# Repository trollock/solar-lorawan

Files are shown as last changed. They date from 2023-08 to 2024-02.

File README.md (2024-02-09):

# Repository Introduction

The following repository contains all of the necessary hardware, software, TTN interface, 3D printing files, and assembly instructions for the CMWX-based LoRaWAN GPS radiotransmitter.

# 1. Hardware 

- datasheets for individual components found in subfolder https://github.com/trollock/solar-lorawan/tree/main/3_hardware

- design files found in subfolder https://github.com/trollock/solar-lorawan/tree/main/5_design_files
- produced in Autodesk Fusion 360 in *.fsch, *.fbrd, and *.f3z formats
  
- production settings:
  + 24.9 x 10.5 mm, 2 layers, 0.4 mm FR4, 0.2 mm min hole size, immersion gold (ENIG) surface finish (1U"), 0.06 mm min track spacing, 1 oz Cu finished copper



# 2. LoRaWAN Network IDs 

- Example based on connecting to The Things Network (TTN) for Europe EU868 Band
- Create a free TTN User account (not the Things Stack)
  + Become familiar with the basics of LoRa and LoRaWAN https://www.thethingsnetwork.org/docs/lorawan/

- Create an application for your devices

- Registering a new device
  + Click "_Enter the device specifics manually_" radio button
  + Click the frequency plan "_Europe 863-870 MHz (SF9 for RX2 - recommended)_"
  + Click the LoRaWAN version "_LoRaWAN Specification 1.0.2_"
  + Click the Regional Parameters version "_RP001 Regional Parameters 1.0.2 revision B_"
  + Create a unique 64 bit JoinEUI for your device (can be shared amongst devices, can be random)  
  + Click "_Generate_" to create a 64-bit random DevEUI
  + Click "_Generate_" to create a 128-bit random AppKEY (can be shared amongst devices)
    + Keep the JoinEUI, DevEUI, and AppKEY to copy into the Arduino example file  
  + Click "_Register End Device_" to create your new device
  
  + see example image below 



# 3. Programming 

- programmed using a combination of Arduino, STM32CubeProgrammer, and an ST-Link.
  + *.elf files are first generated in Arduino, then loaded into STM32CubeProgrammer connected via an ST-Link 
- built on the Arduino core found here https://github.com/GrumpyOldPizza/ArduinoCore-stm32l0
  + comfirmed using a Mac running macOS Big Sur
- basic arduino example found in subfolder XXXX
  + can be modified and them compiled

## Basic programming example

- Open the default example in Arduino IDE found in subfolder "sample_software" https://github.com/trollock/solar-lorawan/tree/main/4_software
- Copy and paste the correct JoinEUI, DevEUI, and AppKEY created earlier under "_Registering a new device_"
  + This can be found on lines 42 - 46 of the example *.ino file provided.
 
  + see example image below



  + click "verify" and then find path to location of *.elf file
  + before opening STM32CubePorgrammer, connect the ST-Link to a suitable port
    + confirm the ST-Link is connected in STM32CubeProgrammer in the upper right under "ST-Link configuration"
  + provide 3.3v power to the device and click "Connect" in STM32CubeProgrammer
  + click "Open File" in STM32CubeProgrammer and find the location of the *.elf file generated earlier by Arduino
  + click "Download" in STM32CubeProgrammer and wait ~ 2-3 seconds until finished 
  + click "Disconnect" in STM32CubeProgrammer
 
  + see example image below
 
  compile

# 4. 3D Printed Housing

- design files for 3D printed housings found in subfolder https://github.com/trollock/solar-lorawan/tree/main/6_housings
- printed on Formlabs Form 3+ / 3B+ at a 0.05 mm micron layer height
- *.stl file sliced in Preform 3.33.1
  + sample print file with supports provided

- Version A for IXOLAR KXOB based solar cells (with PCB adapter)

Housing_A

- Version B for raw GaInAs triple junction solar cells (no adapter necessary)

# 5. Assembly

# 6. Data Access

- log into your new TTN account and click on your application

- Payload Formatter
  + copy the data from the file "payload_formatter_uplink.txt" in the subfolder 2_scripts https://github.com/trollock/solar-lorawan/tree/main/2_scripts
  + click "formatter type" and select Custom Javascript formatter.
  + Delete the code in the paylod formatter box
  + Paste the data from the file "payload_formatter_uplink.txt"
  + Click "Save Changes"

  + see example image below
    


- Storage Integration
  + Click on the leftside menu "Integrations" and then click "Storage Integration"
  + Cliack on the radio button "Activate Storage Integration"
  + The status should say "The storage integration is currently activated"

- API Keys
  + API keys are used for accessing the storage API in a secure manner from another process or service (e.g. [R] )
  + Click the radio button "+ Add API Key"
  + Save this information in a secure place for later
 
- 
- files for accessing stored

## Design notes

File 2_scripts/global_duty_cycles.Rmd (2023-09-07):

---
title: "TTFF / Warm Fixes"
author: "XXXXXX"
date: '2023-05-03'
output: html_document
---

```{r setup, include=FALSE}
knitr::opts_chunk$set(echo = TRUE)

require(readr)
require(tidyverse)
require(ggplot2)
```

```{r, include=FALSE}
df <- list.files(path="//Users/ryanshipley/Documents/Research/2023_CMWX_Radiotags/Data", full.names = TRUE) %>% 
  lapply(read_csv) %>% 
  bind_rows %>%
  dplyr::mutate(time_stamp = lubridate::ymd_hms(message_time)) %>%
  dplyr::distinct(time_stamp, .keep_all=TRUE) %>%
  dplyr::filter(latitude > 0)
```

```{r}
df <- df %>%
  group_by(id) %>%
  arrange(message_time, .by_group = TRUE) %>%
  mutate(time_to_fix = message_time - lag(message_time, default = first(message_time)))
         
df$time_to_fix <- as.numeric(df$time_to_fix)

df$interval <- 
  ifelse (df$time_to_fix > 600 & df$time_to_fix < 800, 
      10,
  ifelse(df$time_to_fix > 1200 & df$time_to_fix < 1400, 
      20,
  ifelse (df$time_to_fix > 1800 & df$time_to_fix < 2000,
      30,
  ifelse (df$time_to_fix > 3600 & df$time_to_fix < 3900,
      60,
  ifelse (df$time_to_fix > 7200 & df$time_to_fix < 7400,
      120,
  ifelse (df$time_to_fix > 10800 & df$time_to_fix < 11200,
      180,
  ifelse (df$time_to_fix > 21600 & df$time_to_fix < 21800,
      360,
      NA)))))))

df$time_to_fix <- 
  ifelse (df$time_to_fix > 600 & df$time_to_fix < 800, 
      df$time_to_fix - 600,
  ifelse(df$time_to_fix > 1200 & df$time_to_fix < 1400, 
      df$time_to_fix - 1200,
  ifelse (df$time_to_fix > 1800 & df$time_to_fix < 2000,
      df$time_to_fix - 1800,
  ifelse (df$time_to_fix > 3600 & df$time_to_fix < 3900,
      df$time_to_fix - 3600,
  ifelse (df$time_to_fix > 7200 & df$time_to_fix < 7400,
      df$time_to_fix - 7200,
  ifelse (df$time_to_fix > 10800 & df$time_to_fix < 11200,
      df$time_to_fix - 10800,
  ifelse (df$time_to_fix > 21600 & df$time_to_fix < 21800,
      df$time_to_fix - 21600,
      NA)))))))

df <- df %>%
      filter(time_to_fix < 180)
```

```{r}
ggplot(df, aes(as.factor(hdop),time_to_fix))+
  geom_boxplot()
```

```{r}
fix_summary <- df %>%
            group_by(interval) %>%
            summarize(n = n(), mean = mean(time_to_fix, na.rm=T), sd = sd(time_to_fix, na.rm=T))
```

```{r}
require(sf)

start <- data.frame(lat = c(46.83353642366947),
                    lon = c(8.182752723850907)) %>% 
  sf::st_as_sf(coords = c("lon", "lat"), crs = 4326)

df <- df %>%
        sf::st_as_sf(coords = c("longitude", "latitude"), crs = 4326)

distance <- data.frame(distance = t(sf::st_distance(start, df, by_element = FALSE)))

df <- cbind(df, distance)

acc_summary <- df %>%
            group_by(hdop) %>%
            summarize(n = n(), mean = mean(distance, na.rm=T), sd = sd(distance, na.rm=T)) 

centroid_summary <- df %>%
            group_by(hdop) %>%
            summarize(geometry = st_union(geometry)) %>% 
            st_centroid

cents <- as.data.frame(st_coordinates(centroid_summary))

centroid_summary <- cbind(centroid_summary, cents)

centroid_distance <- data.frame(distance = t(sf::st_distance(start, centroid_summary, by_element = FALSE)))

```

```{r}
start2 <- st_transform(start, crs = 28992)
start2 <- as.data.frame(st_coordinates(start2))

df2 <- st_transform(df, crs = 28992)
df2 <- as.data.frame(st_coordinates(df2))

df2$X <- df2$X - start2$X
df2$Y <- df2$Y - start2$Y
 
df <- cbind(df, df2)
```

```{r}
require(ggdensity)
require(ggforce)
library(magrittr)

# constants
axis_begin  <- -350
axis_end    <- 350
total_ticks <- 11

# chart junk data
tick_frame <- 
  data.frame(ticks = seq(axis_begin, axis_end, length.out = total_ticks), 
             zero=0) %>%
  subset(ticks != 0)

lab_frame <- data.frame(lab = seq(axis_begin, axis_end, length.out = total_ticks),
                        zero = 0) %>%
  subset(lab != 0)

tick_sz <- (tail(lab_frame$lab, 1) -  lab_frame$lab[1]) / 128

```

```{r}
ggplot(df, aes(X,Y)) + 
    # CHART JUNK
  # y axis line
  geom_segment(x = 0, xend = 0, 
               y = lab_frame$lab[1], yend = tail(lab_frame$lab, 1),
               size = 0.25, color="grey90") +
  # x axis line
  geom_segment(y = 0, yend = 0, 
               x = lab_frame$lab[1], xend = tail(lab_frame$lab, 1),
               size = 0.25, color="grey90") +
  # x ticks
  geom_segment(data = tick_frame, 
               aes(x = ticks, xend = ticks, 
                   y = zero, yend = zero + tick_sz), color="grey90") +
  # y ticks
  geom_segment(data = tick_frame, 
               aes(x = zero, xend = zero + tick_sz, 
                   y = ticks, yend = ticks), color="grey90") + 
  geom_circle(aes(x0 = 0, y0 = 0, r = 140), inherit.aes = FALSE, color="grey90", linetype="dotted") +
  geom_circle(aes(x0 = 0, y0 = 0, r = 210), inherit.aes = FALSE,  color="grey90", linetype="dotted") +
  geom_circle(aes(x0 = 0, y0 = 0, r = 280), inherit.aes = FALSE,  color="grey90", linetype="dotted") +
  geom_point(size=0.01, color="grey50") +
  geom_hdr_lines(data=df[ which(df$hdop == 30), ],  method="freqpoly",  aes(X,Y), color="#440154", size=0.5, probs=0.90, n=500, alpha=0.75) +
  geom_hdr_lines(data=df[ which(df$hdop == 20), ],  method="freqpoly",  aes(X,Y), color="#29af7f", size=0.5, probs=0.90, n=500, alpha=0.75) +
  geom_hdr_lines(data=df[ which(df$hdop == 10), ], method="freqpoly",  aes(X,Y), color="#FDE725", size=0.5, probs=0.90, n=500, alpha=0.75) +
  theme_void()+
  coord_fixed(xlim=c(-350, 350), ylim=c(-350, 350)) +
    # labels
  geom_text(data=lab_frame, aes(x=lab, y=zero, label=lab),
            family = 'Arial', vjust=1.5, color="grey70") +
  geom_text(data=lab_frame, aes(x=zero, y=lab, label=lab),
            family = 'Arial', hjust=1.25, color="grey70")
```

```{r}
setwd("//Users/ryanshipley/Documents/Research/2023_CMWX_Radiotags/Lab_Light_Measurements")

irr <- read.csv("irradiance.csv")

irr_mdl <- glm(Power ~ Irradiance, data=irr)

energy_plot <- ggplot(data=irr, aes(Power / 1000, Irradiance)) +
  geom_smooth(se=FALSE, color="grey80", size=0.5) +
  geom_jitter(size=0.2)+
  cowplot::theme_cowplot() +
  ylab(expression(Irradiance ~ W/m^-2)) +
  xlab ("Charge Current (mA)") +
  scale_x_log10()+
  scale_y_log10()+
  annotation_logticks()+
  geom_hline(yintercept = 75, linetype="dotted", color="grey80") + 
  geom_hline(yintercept = 175, linetype="dotted", color="grey80") + 
  geom_hline(yintercept = 500, linetype="dotted", color="grey80")

energy_plot

```

```{r}
# install and load the solrad package
#install.packages("solrad")
library(solrad)

DOY <- seq(-1, 365, .01)

# define the latitude range
lat_range <- seq(-90, 90, by = 0.5)

# loop over latitudes to calculate irradiance for each time step
irradiance_data <- lapply(lat_range, function(lat) {
  radiation <- OpenRadiation(DOY, Lat = lat, Lon=0, SLon=0, DS=0, Elevation = 100)
})

# combine the results into a matrix
#irradiance_matrix <- matrix(do.call(cbind, irradiance_data))

#irradiance_matrix <- oce::matrixSmooth(irradiance_matrix, 500)

irradiance_matrix <- as.data.frame(do.call(cbind, irradiance_data))

# set the row names as latitude values
row.names(irradiance_matrix) <- DOY

# set the column names as datetime values
colnames(irradiance_matrix) <- lat_range

irradiance_matrix <- cbind(DOY, irradiance_matrix)

irradiance_matrix <- reshape2::melt(irradiance_matrix, id=c("DOY"))

irradiance_matrix$DOY_bin <- ceiling(irradiance_matrix$DOY)

irradiance_summary <- irradiance_matrix %>%
                        dplyr::group_by(DOY_bin, variable) %>%
                        dplyr::summarize(mean = mean (value, na.rm=T)) %>%
                        dplyr::filter(DOY_bin > 0) %>%
                        dplyr::filter(mean > 0)

irradiance_summary <- irradiance_summary %>%
                        pivot_wider(names_from = variable, values_from = mean)

irradiance_summary <- as.matrix(irradiance_summary[, -1])

irradiance_summary <- oce::matrixSmooth(irradiance_summary, 3)

colnames(irradiance_summary) <- lat_range

irradiance_summary <- as.data.frame(cbind(DOY = seq(1,365, 1), irradiance_summary))

irradiance_summary <- reshape2::melt(irradiance_summary, id=c("DOY"))

irradiance_summary <- irradiance_summary %>%
                        dplyr::filter(!is.na(value))

irradiance_summary$variable <- as.numeric(levels(irradiance_summary$variable))[irradiance_summary$variable]
```

```{r}
cold_fix_mean <- 45

irradiance_summary$harv_30 <- ifelse(irradiance_summary$value == 0, 0, ((irr_mdl$coefficients[2] * (irradiance_summary$value)) - irr_mdl$coefficients[1]) * 0.3)
irradiance_summary$time_fx_30 <- ifelse(irradiance_summary$harv_30 == 0, 0, 1440 / (((cold_fix_mean * 32000) / irradiance_summary$harv_30 ) / 60 ))
 
irradiance_summary$harv_05 <- ifelse(irradiance_summary$value == 0, 0, ((irr_mdl$coefficients[2] * (irradiance_summary$value)) - irr_mdl$coefficients[1]) * 0.05)
irradiance_summary$time_fx_05 <- ifelse(irradiance_summary$harv_05 == 0, 0, 1440 / (((cold_fix_mean * 32000) / irradiance_summary$harv_05 ) / 60 ))

duty_01_plot <- ggplot(irradiance_summary, aes(DOY, variable, z=time_fx_05)) +
                geom_raster(fill="white", color="white") +
                #geom_contour(aes(colour = after_stat(level))) +
                metR::geom_contour2(aes(z = time_fx_05, label = stat(level), colour = after_stat(level)), breaks=c(6,8,10,12,14,16,18,20,22,24,26)) +
  scale_colour_viridis_c() + 
                cowplot::theme_cowplot() +
                xlab("Day of Year") +
                ylab( "Latitude") +
  theme(legend.position = "none") +
  scale_y_continuous(expand = c(0,0), breaks=c(-90, -60, -30, 0 , 30, 60, 90)) +
  scale_x_continuous(expand = c(0,0), breaks=c(1, 60, 120, 180, 240, 300, 360)) +
  theme(panel.background = element_rect(fill = 'grey80', colour = 'grey80'))

duty_01_plot
```

```{r}
cowplot::plot_grid(energy_plot, duty_01_plot, align = 'h')
```

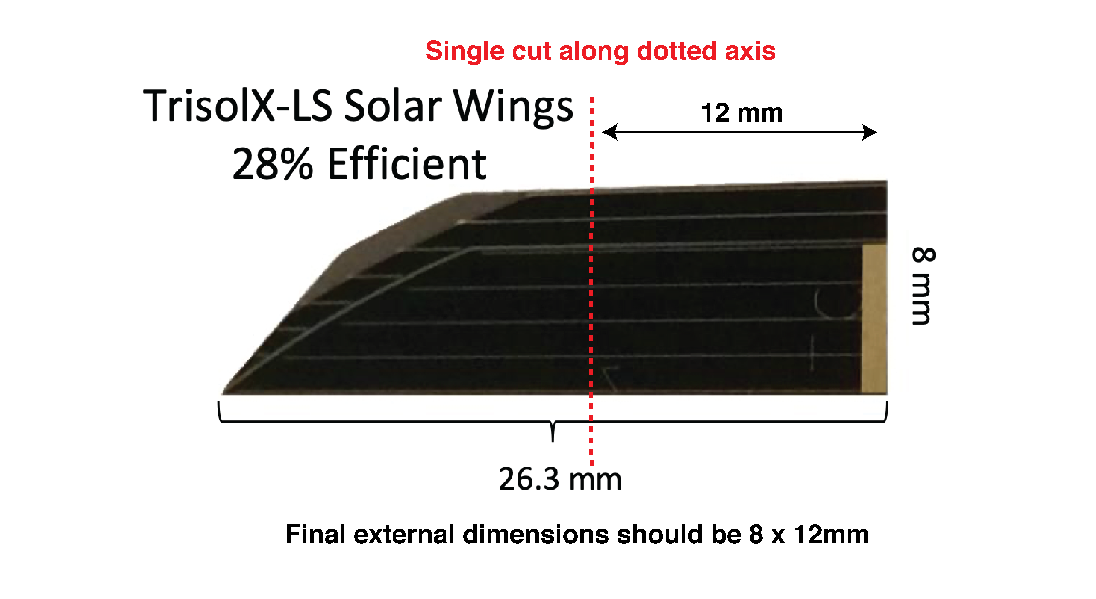
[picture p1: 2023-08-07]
3_hardware/TrisolX/Cut Dimensions/TrisolX.png

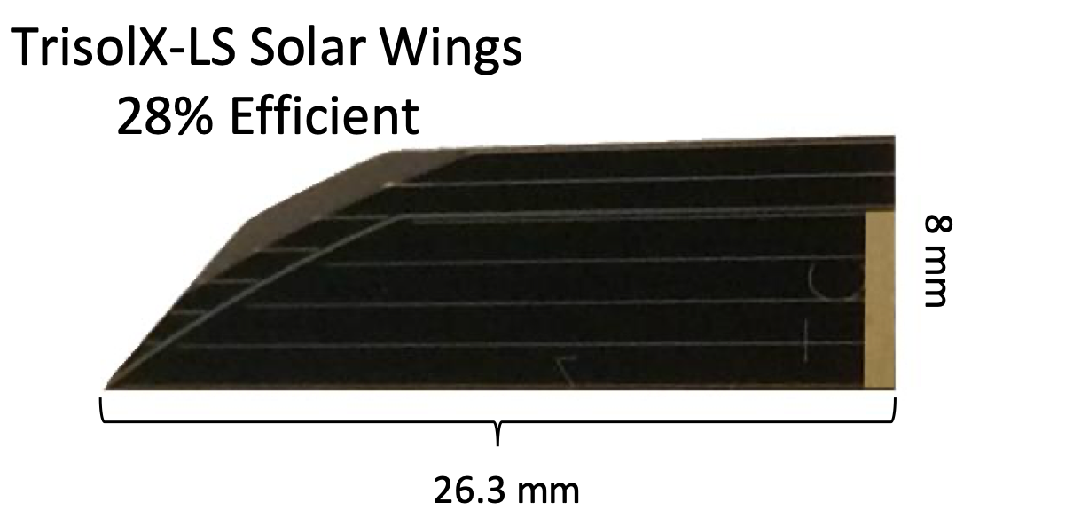
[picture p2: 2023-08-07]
3_hardware/TrisolX/Screen Shot 2023-04-20 at 6.27.21 PM.png

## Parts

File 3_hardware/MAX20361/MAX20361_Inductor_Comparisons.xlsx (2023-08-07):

Inductors for the MAX201361
Recommended
Manufacturer | Part Number | Inductance | V | I | Isat | DCR | Resonance | Dimensions
Murata | DFE201612E-4R7M=P2 | 4.7 | 20 | 1.2 | 1.8 | 0.252 | 1 MHz | 2 x 1.6 x 2
Murata | DFE252010F-4R7M=P2 | 4.7 | 20 | 1.4 | 1.9 | 0.24 | 1 MHz | 2.5 x 2 x 1
Wurth | 744043004 | 4.7 |  | 1.55 | 1.7 | 0.05 | 60 MHz | 4.8 x 4.8 x 3
Wurth | 744031150 | 15 |  | 0.45 | 0.62 | 0.255 | 30 MHz | 3.8 x 3.8 x 1.8
Wurth | 7447779122 | 22 | 120 | 1.41 | 1.7 | 0.09 | 17 MHz | 7.3 x 7.3 x 4.5
Coildcraft | XFL2010-223MR | 22 |  | 0.16 | 0.31 | 1.3 |  | 2.0 x 1.0
Coilcraft | LPS3015-223MR | 22 |  | 0.42 | 0.5 | 0.83 |  | 3.13 x 3.13 x 1.5
Coilcraft | LPS3030-223 | 22 |  | 0.42 | 0.48 | 0.31 |  | 3.15 x 3.15 x 3
Murata | LQH44PN220MPR# (https://www.murata.com/en-global/products/productdetail?partno=LQH44PN220MPR%23) | 22 |  | 0.9 | 1.05 | 0.348 |  | 4 x 4 x 1.65
Wurth | 744031220 | 22 |  | 0.36 | 0.51 | 0.41 |  | 3.8 x 3.8 x 1.8
Wurth | 744025220 | 22 |  | 0.5 | 0.75 | 0.525 |  | 2.8 x 2.8 x 2.8
Wurth | 744043220 | 22 |  | 0.7 | 0.925 | 0.16 |  | 4.8 x 4.8

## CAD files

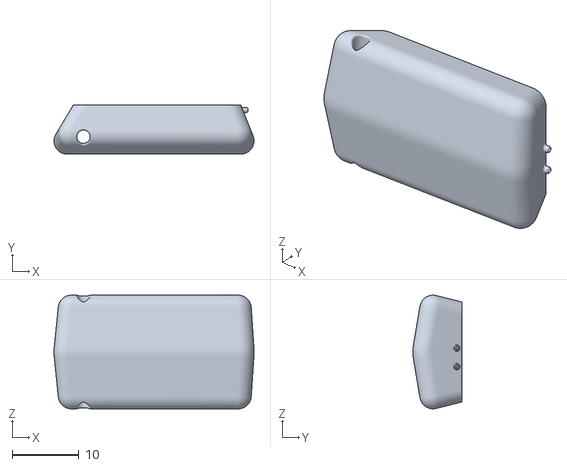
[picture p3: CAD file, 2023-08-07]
6_housings/v27_housing.stl
30.0 x 7.43 x 17.1

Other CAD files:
3_hardware/TrisolX/TrisolX_cell.dwg

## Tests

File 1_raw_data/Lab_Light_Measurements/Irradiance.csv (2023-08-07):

Irradiance | Irr2 | Power | Power2
52 | 52 | 245 | 227
52 | 49 | 240 | 227
52 | 48 | 243 | 256
52 | 51 | 249 | 258
52 | 57 | 237 | 248
68 | 72 | 488 | 456
68 | 65 | 481 | 446
68 | 71 | 493 | 501
68 | 63 | 499 | 510
68 | 71 | 483 | 497
84 | 81 | 740 | 794
84 | 91 | 743 | 772
84 | 81 | 732 | 672
84 | 77 | 728 | 724
84 | 87 | 734 | 744
103 | 109 | 1022 | 1049
103 | 102 | 1026 | 1113
103 | 111 | 1031 | 1084
103 | 108 | 1018 | 975
103 | 112 | 1027 | 970
126 | 121 | 1379 | 1244
126 | 120 | 1374 | 1295
126 | 134 | 1383 | 1447
126 | 123 | 1372 | 1375
126 | 127 | 1382 | 1340
163 | 153 | 1945 | 1896
163 | 152 | 1932 | 2006
163 | 158 | 1936 | 1772
163 | 172 | 1951 | 1787
163 | 149 | 1953 | 2052
219 | 228 | 2805 | 2736
219 | 236 | 2793 | 2569
219 | 214 | 2799 | 2857
219 | 239 | 2808 | 2647
219 | 215 | 2807 | 2534
276 | 274 | 3677 | 3389
276 | 293 | 3663 | 3833
276 | 253 | 3689 | 3459
276 | 253 | 3672 | 3937
276 | 285 | 3667 | 3745
331 | 305 | 4520 | 4145
331 | 310 | 4511 | 4062
331 | 308 | 4518 | 4729
331 | 335 | 4532 | 4388
331 | 305 | 4529 | 4833
435 | 446 | 6101 | 5934
435 | 432 | 6213 | 6270
435 | 456 | 6119 | 6225
435 | 456 | 6202 | 5928
435 | 394 | 6127 | 5800
632 | 639 | 9130 | 8363
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

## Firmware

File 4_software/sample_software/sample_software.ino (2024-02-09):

/* LoRa GPS Receiver (needs a better name)
rev 0.1 J R Shipley 26/12/2020 
The state machine contains 4 basic parts - 1) sleep mode (slp_mode), 2) gps mode (gps_mode), 3) transmit mode (tx_mode) and 
receive mode (rx_mode).
We will use a set of different basic counters to determine how long it should attempt to obtain a gps fix 
In the future, it would be ideal component to implement a simplified version of a PID controller to determine the 
trajectory of the battery charge state, to make basic predictions on future charge states, and the amount of time
that should be dedicated to getting a fix.

Hardware changes 
rev 0.1 - changed the ZOE-M8Q RAM backup to use a dedicated I/O on the CMWX module, so we can turn off 
battery RAM backup if the ephemeris has expired.  This would reduce the power consumption from 18 to 2.2 uA when it
has been greater than 4 hours since the last ephemeris update.

rev 0.2 - scrapped the UBlox related code, switch to use Quectel L70 to save on power and $$$, active searching current is 14.1 mA on the demo module, sleep mode
battery backup RAM is only 12.9 uA. 

rev 0.3 - added the CAT24 EEPROM to write all data that isn't immediately able to be sent, then checks later if gateway is within range and sends historical data  

rev 1.0 - added the LG77L GPS module, switched GPS REST pin from 3 to 2, don't measure lithium poly under load with LC709203!
*/ 
#include <TinyGPS++.h>
#include "STM32L0.h"
#include "LoRaWAN.h"
#include <Wire.h>
#include <extEEPROM.h>    //https://github.com/PaoloP74/extEEPROM
#include <SparkFun_MAX1704x_Fuel_Gauge_Arduino_Library.h>
#include "SparkFun_BMP581_Arduino_Library.h"

TinyGPSPlus gps;

SFE_MAX1704X lipo(MAX1704X_MAX17048); //create a gas gauge object

BMP581 pressureSensor; // Create a pressure sensor object

//!!! This is different on the demo board, it is the DEFAULT and not the SECONDARY address
//uint8_t i2cAddress = BMP581_I2C_ADDRESS_DEFAULT; // 0x47
uint8_t i2cAddress = BMP581_I2C_ADDRESS_SECONDARY; // 0x46

//LoRaWAN provisioning data
//---------------------------------------------------------------------------------------------------------
const char *appEui = "0000000000000000";

//test board data
const char *appKey = "8836AAE8CBDF34101AC94EAFA8F94575"; 
const char *devEui = "70B3D57ED0063AB7"; 

//defines for the serial - Quectel interface - GPS related globals
//---------------------------------------------------------------------------------------------------------
#define GPSTX 1 //pin number for GPS TX output - data from Arduino to GPS
#define GPSRX 0 //pin number for GPS RX input - from GPS to Arduino 
static const uint32_t GPSBaud = 9600;

// board definitions for the power and reset for the GPS module
#define GPS_PIN A2  // pin 24
#define GPS_RST 2 // pin 39

//some basic state machine related vars
enum State_enum {SLEEP_MODE, STARTUP_MODE, GPS_MODE, TX_RX_MODE, HIST_MODE}; 
uint8_t state = STARTUP_MODE; 

//time keeping related, including sleep timers and GPS timeouts
unsigned long startTime = 0;
unsigned int slp_time = 60000 * 240;
unsigned int hist_time = 8000;
unsigned int gps_timeout = 60000 * 3; //5 minutes = 300,000 milliseconds, demo 30 seconds

uint8_t payload[21] = {0, 0, 0, 0, 0, 0, 0, 0, 0, 0, 0, 0, 0, 0, 0, 0, 0, 0, 0, 0, 0};

uint8_t   Status = 0;           // 1 bit
uint8_t   Month = 12;           // 4 bits
uint8_t   Day = 31;             // 5 bits 
uint8_t   Year = 99;            // 7 bits
uint8_t   Hour = 23;            // 5 bits
uint8_t   Minute = 59;          // 6 bits
uint8_t   Second = 59;          // 6 bits but reduced to value between 1 and 12 (5 second accuracy) i.e. 4 bits
int32_t   Latitude = 46833722;  // 3 bytes 
int32_t   Longitude = 8183062;  // 3 bytes
uint8_t   Hdop = 124;           // 1 byte
uint16_t  Volts = 173;          // 2 bytes
uint32_t  Pressure = 0;         // 24 bits
uint16_t  Temp = 402;           // 8 bits

uint8_t Temp_tx = 255;

int32_t   prev_Longitude = 0;
uint8_t   Siv = 0;
uint8_t   Siv_thresh = 4;

bool gps_fix = false;
bool has_data = false;
bool in_range = false;
bool has_join = false;
bool sleep_flag = false;

uint8_t rem_data = 0;

//voltage measurement 
//---------------------------------------------------------------------------------------------------------
#define VOLTS_PIN A3  // pin 24

uint16_t sensorValue = 0;
float voltage = 0;
uint16_t volts = 0;
uint16_t old_volts = 0;

//some globals for the CAT24 EEPROM module
//---------------------------------------------------------------------------------------------------------
//One 24LC256 EEPROMs on the bus
const uint32_t totalKBytes = 32;         //for read and write test functions
extEEPROM eep(kbits_512, 1, 128, 0x50);         //device size, number of devices, page size, i2c address

// variables stored on the EEPROM
uint8_t  has_data_address = 0;
uint16_t last_save_address = 1;
uint16_t last_sent_address = 3;
uint8_t init_start_address = 5;

//start eeprom storage on 6
// variables not stored on EEPROM
uint8_t save_offset = 6;
uint16_t curr_sent = 0;
uint16_t sent_counter = 5;
uint16_t max_counter = 0;
uint16_t max_send = 5;
uint16_t last_save = 0;
uint16_t last_save_idx = 0;
uint16_t last_sent = 0;
uint16_t last_sent_idx = 0;

//---------------------------------------------------------------------------------------------------------
//---------------------------------------------------------------------------------------------------------

void setup(){ 
         uint8_t eepStatus = eep.begin(eep.twiClock400kHz);   //go fast!
          if (eepStatus) 
          {
            while (1);
          }

          //for (int i = 1; i < 1000; i++){
          //  eep.write(i, 1);
          //}

         //initialize the EEPROM for after first startup post programming
          uint8_t init_start = eep.read(init_start_address);
          if (init_start != 0) 
          {
            writeIntEEPROM(last_save_address, 0);      
            writeIntEEPROM(last_sent_address, 0);
            //write a zero because the eeprom starts with FEFE or FFFF, a zero means it's not the first time it started
            eep.write(init_start_address, 0);
            init_lora();
          }
          STM32L0.stop(5000);
}

void loop() {
  switch (state) {
       case STARTUP_MODE:
          Wire.begin();
          eep.begin(eep.twiClock400kHz);
          lipo.begin();
          init_pins();
          batt_check();
          sleep_flag = false;
          duty_cycle();
          
         if (sleep_flag == true)
         {
          state = SLEEP_MODE;
         }
         else 
         {
          if (!LoRaWAN.joined())
          {
          init_lora(); 
          } 
          init_gps();
          startTime = millis();
          state = GPS_MODE;
         }
          break; 
    
       case GPS_MODE:
          if (millis() - startTime <= gps_timeout && gps_fix == false)
          {
            smartDelay(1000);
            
            //time related variables from the GPS module fix
            Status  = 0;
            Month   = gps.date.month();
            Day     = gps.date.day();
            Year    = (uint16_t) gps.date.year() - 2000;
            Hour    = gps.time.hour();
            Minute  = gps.time.minute();
            Second  = gps.time.second();

            //Spatial variables of the GPS module fix
            Latitude = (float) gps.location.lat() * 10000000;
            Longitude = (float) gps.location.lng() * 10000000;
            Hdop = (float) (gps.hdop.hdop() * 10);
            Siv = gps.satellites.value();

              if (Siv >= Siv_thresh && Longitude != prev_Longitude)
              {
                gps_fix = true;
                digitalWrite(GPS_PIN, LOW);
                prev_Longitude = Longitude;
                state=TX_RX_MODE;
              }  
              else 
              {
              gps_fix = false;
              }    
          } 
          else 
          {
            digitalWrite(GPS_PIN, LOW);
            state = TX_RX_MODE;
          } 
          break;
    
      case TX_RX_MODE:
          delay(50);
          stored_data(); //this provides has_data, last_sent, and last_save updates 
          pressure_check();
          if (LoRaWAN.joined() && !LoRaWAN.busy())
          {
            create_Packet(payload);
            LoRaWAN.beginPacket();
            LoRaWAN.write(payload, sizeof(payload));  
            LoRaWAN.endPacket(true); 
              while (LoRaWAN.busy())
              {
              STM32L0.sleep(1000);
              }   
              if (LoRaWAN.confirmed())
              {
                in_range = true;
              }
              else  //goes here after first handshake fail
              {   
                in_range = false;
                save_Packet(payload);
              }
          }
          if (has_data && in_range)
          {
            state = HIST_MODE;  
          }
          else 
          {
            state = SLEEP_MODE;
          }
          break;  

       case HIST_MODE:
         if (LoRaWAN.joined() && !LoRaWAN.busy() && has_data)
            {
              for (int i = 0; i < sent_counter; i++)
              {
                Wire.begin();
                eep.begin(eep.twiClock400kHz);
                read_Packet(payload);
                  LoRaWAN.beginPacket();
                  LoRaWAN.write(payload, sizeof(payload));  
                  LoRaWAN.endPacket(false);
                STM32L0.stop(hist_time);
              }
            }
          state = SLEEP_MODE;
          break;   

      case SLEEP_MODE:
          init_sleep();
          STM32L0.stop(slp_time);
          state = STARTUP_MODE;
          break; 
  }
}

void init_pins (void) {  
      Serial1.begin(GPSBaud);
      //pinMode(A0, INPUT);
      pinMode(GPS_PIN, OUTPUT);
        digitalWrite(GPS_PIN, LOW);
      pinMode(GPS_RST, OUTPUT);
        digitalWrite(GPS_RST, LOW);
}

void init_lora (void) {
    LoRaWAN.begin(EU868);
    LoRaWAN.setDutyCycle(false);
    LoRaWAN.setADR(false);
    LoRaWAN.setDataRate(0);
    LoRaWAN.setTxPower(17);
    LoRaWAN.setAntennaGain(0.5);
    LoRaWAN.setReceiveDelay(4000);
    LoRaWAN.setJoinRetries(2);
    LoRaWAN.setRetries(2);
    LoRaWAN.joinOTAA(appEui, appKey, devEui);
}

void init_gps (void) {
    digitalWrite(GPS_PIN, HIGH);
    digitalWrite(GPS_RST, HIGH);
      delay(200);
    digitalWrite(GPS_RST, LOW);
      delay(200);
    digitalWrite(GPS_RST, HIGH);
    gps_fix = false; 
    in_range = false;
}

void init_sleep (void) {
          digitalWrite(GPS_PIN, LOW);
          delay(25);
          digitalWrite(GPS_RST, LOW); 
          delay(25);
          Wire.end();
          digitalWrite(SCL, HIGH);
          delay(25);
          digitalWrite(SDA, HIGH);
          delay(25);
          Serial1.end();
          delay(25);
}

uint8_t create_Packet(uint8_t payload [21])
{
  payload[0]  = Status << 7 | Month << 3 | Day >> 2; 
  payload[1]  = Day << 6 | Year >> 1; 
  payload[2]  = Year << 7 | Hour << 2 | Minute >> 4;
  payload[3]  = Minute << 4 | static_cast<int>(floor(Second / 5));
  payload[4]  = Latitude / 100 >> 16; 
  payload[5]  = Latitude / 100 >> 8; 
  payload[6]  = Latitude / 100;
  payload[7]  = Longitude / 100 >> 16;
  payload[8]  = Longitude / 100 >> 8;
  payload[9]  = Longitude / 100;
  payload[10] = Hdop;
  payload[11] = Volts >> 8;
  payload[12] = Volts;
  payload[13] = Pressure >> 16;
  payload[14] = Pressure >> 8;
  payload[15] = Pressure;
  payload[16] = Temp < 510 && Temp > 0 ? Temp / 2 : 255;
  payload[17] = last_save >> 8;
  payload[18] = last_save;
  payload[19] = last_sent >> 8;
  payload[20] = last_sent;
}
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
